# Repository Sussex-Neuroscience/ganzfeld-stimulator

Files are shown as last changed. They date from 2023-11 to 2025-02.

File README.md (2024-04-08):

# ganzfeld-stimulator

## Overview
We built a 'full-field' LED stimulator as a visual stimulus generator for in vivo rodent physiology experiments. The stimulator can generate arbitrary temporal patterns of green and UV light (chromatic channels the mouse visual system is sensitive to) such as high frequency flicker or sinusoidal dimming. Stimulation patterns are generated using PWM signals from a microcontroller.

## Parts 

| Item | Link | Quantity | Cost | Datasheet |
|------|------|----------|------|-----------|
| **LEDS**| | | |
| UV LED   |[C3535U- UNL1-A1G11H-380 TSLC, UV LED, 390nm 480mW 125 °, 2-Pin Surface Mount package](https://uk.rs-online.com/web/p/uv-leds/9033769) | (6 x 6 array) = 36 + any spares | £6.88 each | [From RS](https://uk.rs-online.com/web/p/uv-leds/9033769)|
| Green LED | [ams OSRAM3 V Green LED PLCC 2 SMD, TOPLED LT T673-Q1R2-25](https://uk.rs-online.com/web/p/leds/6648197) | (6 x 6 array) = 36 + any spares | £0.196 each| [From RS](https://uk.rs-online.com/web/p/leds/6648197) |
| LED mounting PCB |  [Custom PCB board for mounting LEDs](repo link) | 6 (Each board is populated with 6 of green and 6 UV) | ?? | 
| Soldering stencil | [Custom stencil](repo link) | 1 | ?? |
|**PSU and Drivers**|||
| LED Driver | [Recom LED Driver, 2 → 35V dc Output, 350mA Output, Constant Current Dimmable](https://uk.rs-online.com/web/p/led-drivers/0416913) | ?? | £12.16 each | [detailed](https://g.recomcdn.com/media/Datasheet/pdf/.fYUQjOlW/.t2a80a771bdbb0ef300f7/Datasheet-93/RCD-24.pdf) |
| PSU | [12V dc Output, 5A Output](https://uk.rs-online.com/web/p/ac-dc-adapters/8808408?gb=s) | ?? | £21.38 each |
|**Box Construction**| | |
| Structure | [MakerBeam starter kit](https://www.technobotsonline.com/makerbeamxl-regular-starter-kit-in-black-anodised-threaded.html) | 1 | £102.95 (possible to buy specific parts separately) | [200mm beam technical drawing](https://drive.google.com/drive/folders/0B8h5C_ek_fmKa2E4a2I1NEtXWTQ?resourcekey=0-tFenALGdWDfK6WEzQJMuUQ), [50mm beam technical drawing](https://drive.google.com/drive/folders/1401xnkoKaVmki9BlENUgdnQiJKWathsU) |
| Structure | [MakerBeam Construction Cubes](https://www.technobotsonline.com/makerbeam-xl-black-corner-cubes-pack-of-12.html) | 1x box of 12 (need 8) |  £18.00 for 12 | [corner cube technical drawing](https://drive.google.com/drive/folders/0B8h5C_ek_fmKcEFvbkl0NWtaZ28?resourcekey=0-kpjmWWiNEXZBVXVSDK05Yg) |
| Reflective Walls + floor | [RS PRO Aluminium Metal Sheet 300mm x 500mm, 2mm Thick](https://uk.rs-online.com/web/p/metal-sheets/0434059) | 1*(200x200mm), 4*(50x200mm) | £49.07 for 5 300x500mm sheets |
|**Diffuser** | | |
| Tracing paper | e.g. [amazon](https://www.amazon.co.uk/GLADFRESIT-Translucent-Architecture-Scrapbooking-Printing/dp/B0C3VX6JPX/ref=asc_df_B0C3VX6JPX/?tag=googshopuk-21&linkCode=df0&hvadid=662823090693&hvpos=&hvnetw=g&hvrand=10142952570193465802&hvpone=&hvptwo=&hvqmt=&hvdev=c&hvdvcmdl=&hvlocint=&hvlocphy=1006565&hvtargid=pla-2196737734548&psc=1&mcid=5f2980b322dd33169770b0c6ecff1379) | 2 sheets + spares | £5.99 |
| Diffusion holder | [Custom 3D printed part](repo link) | ?? | ?? |

## Construction

### Building the stimulator structure
We opted to make a 200x200mm box with a ~50mm depth for achieving a uniform intensity of light. The box can easily be scaled larger and smaller to suit your purposes accordingly.

1) Join 4 x 200mm beams to form a square, using the construction cubes in the corners. You need to make 2 of these for the top and bottom of the box.
2) Cut a ~200x200mm piece of aluminium to slot into the centre of one of the square. You'll need to slightly adjust the size so it fits into the grooves of the beams. This will provide the base for the LED PCBs. (drill a hole of diameter xx for wires)
3) Add 4 x 50mm beams upright to the 4 corners of one of the squares.
4) Screw in the other 200x200mm square to these upright beams to form the top of the box.
5) Cut 4 more pieces of aluminium to form the 4 walls of the box. You want them to be flush with the top of the box to maximise reflectivity of the light inside the box.

### Populating the LEDs on the PCB boards
Use the soldering stencil to populate each of the PCB boards with 6 x green and 6 x UV LEDs. The LEDs are arranged in alternating rows of 3 green/UV.

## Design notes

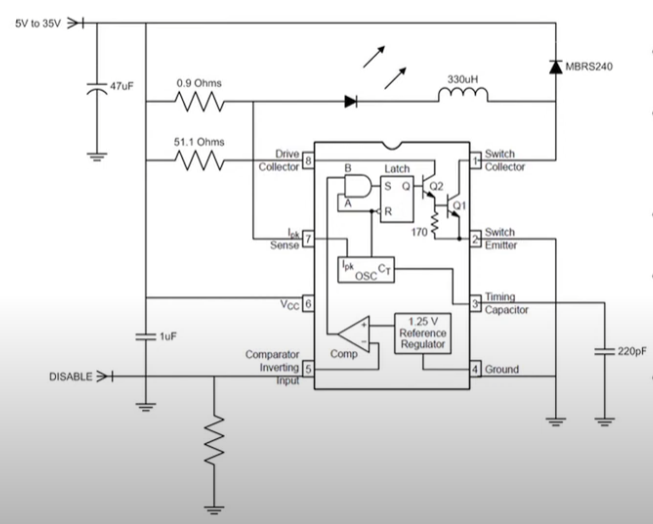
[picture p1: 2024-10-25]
Hardware/PCB/driver circuit.PNG

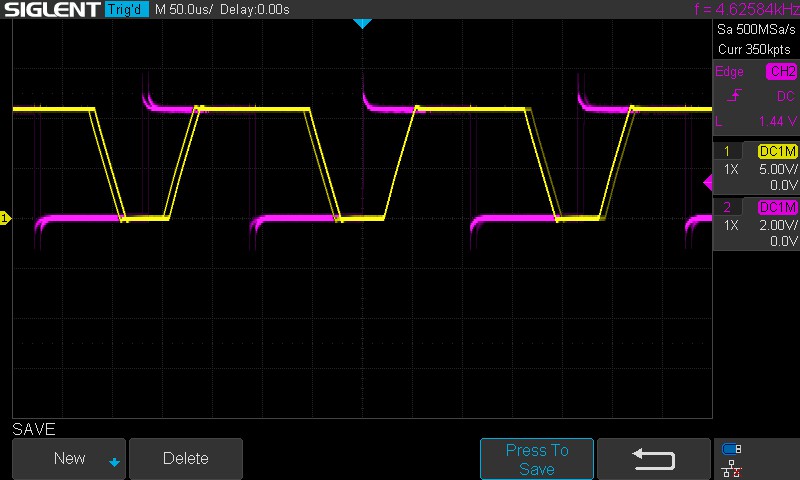
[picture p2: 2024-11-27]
Hardware/PCB/JPG4.62.jpg

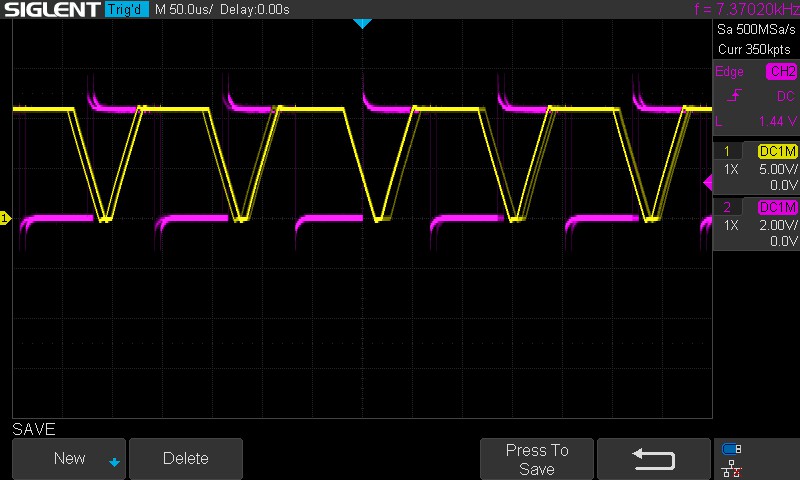
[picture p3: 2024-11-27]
Hardware/PCB/JPG7.37.jpg

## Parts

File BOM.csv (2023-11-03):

qty | component | link
3 | Aluminium sheets | https://uk.rs-online.com/web/p/metal-sheets/0434059
3 | led drivers | https://uk.rs-online.com/web/p/led-drivers/0416913
1 | power supply 12v 5a | https://uk.rs-online.com/web/p/ac-dc-adapters/8808408?gb=s
1 | power connector | https://uk.rs-online.com/web/p/dc-power-connectors/8782606?gb=s
1 | red wire | https://uk.rs-online.com/web/p/hook-up-wire/1225880?gb=s
1 | black wire | https://uk.rs-online.com/web/p/hook-up-wire/1225876?gb=s
2 | pcb board | https://uk.rs-online.com/web/p/copper-clad-boards/2192145?gb=s

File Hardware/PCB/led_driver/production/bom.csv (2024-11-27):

Designator | Footprint | Quantity | Value | LCSC Part #
C1, C5, C6, C8 | CP_Radial_Tantal_D4.5mm_P2.50mm | 4 | 1uF
C2, C3, C4, C7 | CP_Radial_Tantal_D4.5mm_P2.50mm | 4 | C
J1, J3, J4, J8 | JST_XH_B3B-XH-A_1x03_P2.50mm_Vertical | 4 | Conn_01x03_Pin
J2 | JST_XH_B2B-XH-A_1x02_P2.50mm_Vertical | 1 | greenLED
J5, J7, J9 | JST_XH_B2B-XH-A_1x02_P2.50mm_Vertical | 3 | UVLED
J6 | JST_XH_B2B-XH-A_1x02_P2.50mm_Vertical | 1 | power_in
L1, L2, L3, L4 | L_Radial_D6.0mm_P4.00mm | 4 | 22uH
R1, R2, R3, R4 | R_Axial_DIN0411_L9.9mm_D3.6mm_P12.70mm_Horizontal | 4 | R
U1, U2, U3, U4 | Converter_DCDC_RECOM_RCD-24_THT | 4 | RCD-24

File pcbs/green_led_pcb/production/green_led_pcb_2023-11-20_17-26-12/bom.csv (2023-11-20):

Designator | Footprint | Quantity | Value | LCSC Part #
D1, D10, D11, D12, D13, D14, D15, D16, D2, D3, D4, D5, D6, D7, D8, D9 | LED_PLCC-2_3.4x3.0mm_KA | 16 | LED
J1, J2, J3, J4 | PinSocket_1x02_P2.54mm_Horizontal | 4 | Conn_01x02_Socket

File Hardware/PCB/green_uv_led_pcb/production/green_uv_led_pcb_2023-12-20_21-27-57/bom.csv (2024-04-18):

Designator | Footprint | Quantity | Value | LCSC Part #
D1, D10, D11, D2, D3, D9 | LED_PLCC-2_3.4x3.0mm_KA | 6 | LED
D13, D14, D15, D5, D6, D7 | LED_Cree-XP | 6 | LED
H1, H2, H3, H4 | MountingHole_3.2mm_M3 | 4 | MountingHole
J1 | PinSocket_1x02_P2.54mm_Horizontal | 1 | Green bank 1
J2 | PinSocket_1x02_P2.54mm_Horizontal | 1 | UV bank 1
J3 | PinSocket_1x02_P2.54mm_Horizontal | 1 | Green bank 2
J4 | PinSocket_1x02_P2.54mm_Horizontal | 1 | UV bank 2

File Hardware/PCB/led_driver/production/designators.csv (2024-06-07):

C1:1
C2:1
C3:1
C4:1
C5:1
C6:1
C7:1
C8:1
H1:1
H2:1
H3:1
H4:1
J1:1
J2:1
J3:1
J4:1
J5:1
J6:1
J7:1
J8:1
J9:1
L1:1
L2:1
L3:1
L4:1
R1:1
R2:1
R3:1
R4:1
U1:1
U2:1
U3:1
U4:1

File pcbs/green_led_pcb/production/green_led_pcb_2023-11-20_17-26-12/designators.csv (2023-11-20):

D1:1
D10:1
D11:1
D12:1
D13:1
D14:1
D15:1
D16:1
D2:1
D3:1
D4:1
D5:1
D6:1
D7:1
D8:1
D9:1
J1:1
J2:1
J3:1
J4:1

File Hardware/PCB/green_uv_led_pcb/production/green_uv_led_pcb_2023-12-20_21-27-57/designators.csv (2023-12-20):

D1:1
D10:1
D11:1
D13:1
D14:1
D15:1
D2:1
D3:1
D5:1
D6:1
D7:1
D9:1
H1:1
H2:1
H3:1
H4:1
J1:1
J2:1
J3:1
J4:1

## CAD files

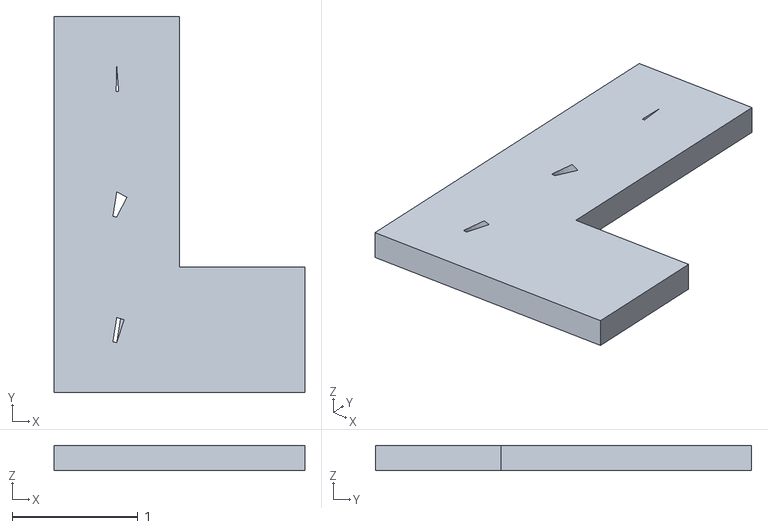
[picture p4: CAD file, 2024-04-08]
3d_printing/3rdPartyParts/LBracketb.stl
2.00 x 3.00 x 0.2

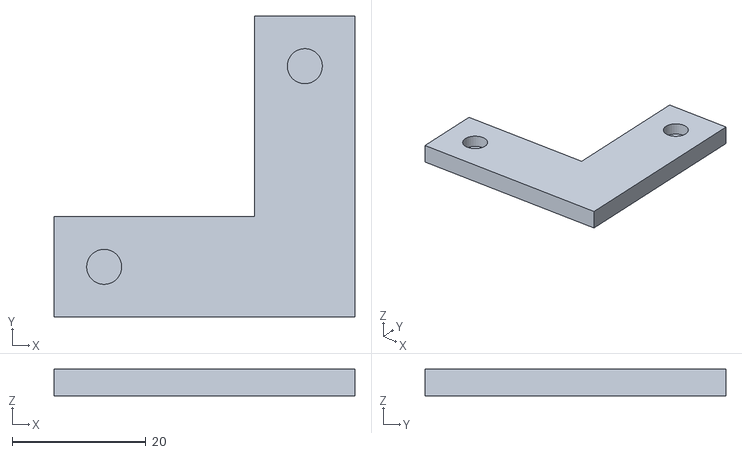
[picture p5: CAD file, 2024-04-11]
3d_printing/CustomRBracket_magnet.stl
45.0 x 45.0 x 4.00

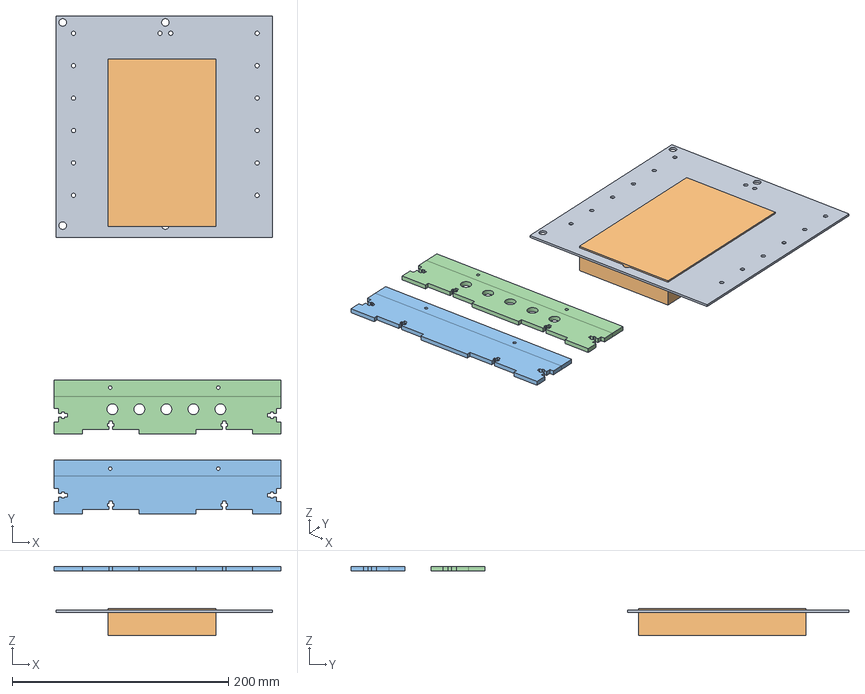
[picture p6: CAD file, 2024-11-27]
Hardware/CAD/Designs/StimulatorHousing.FCStd
210.0 x 461.0 x 64.0 mm
Bottom+holes
Electronics

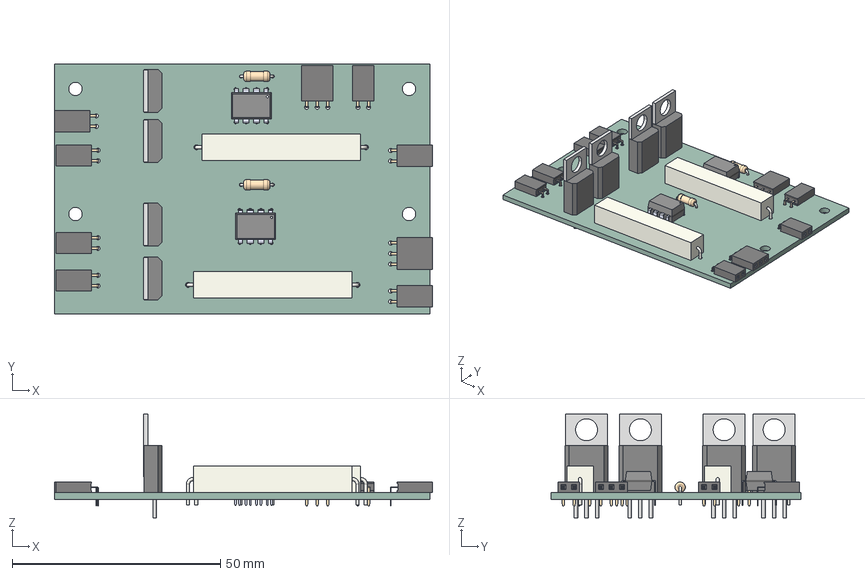
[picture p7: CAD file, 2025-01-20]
Hardware/PCB/custom_driver/custom_driver.step
90.7 x 60.0 x 24.9 mm
PinSocket_1x02_P254mm_Horizontal x 7
R_Axial_DIN0207_L63mm_D25mm_P762mm_Horizontal x 2
P8 x 2
PinSocket_1x03_P254mm_Horizontal x 2
R_Axial_Power_L380mm_W64mm_P4064mm x 2
_autosave-custom_driver_PCB

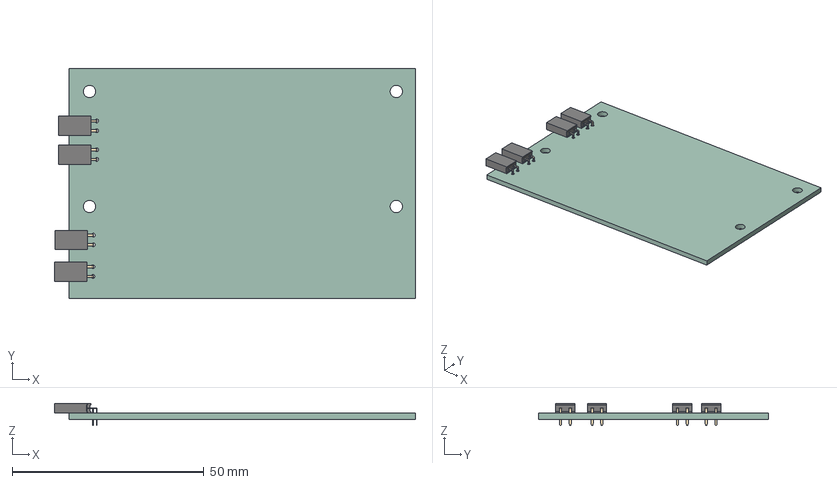
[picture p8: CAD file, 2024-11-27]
Hardware/PCB/green_uv_led_pcb/green_uv_led_pcb.step
94.1 x 60.0 x 5.84 mm
PinSocket_1x02_P254mm_Horizontal x 4
green_uv_led_pcb_PCB

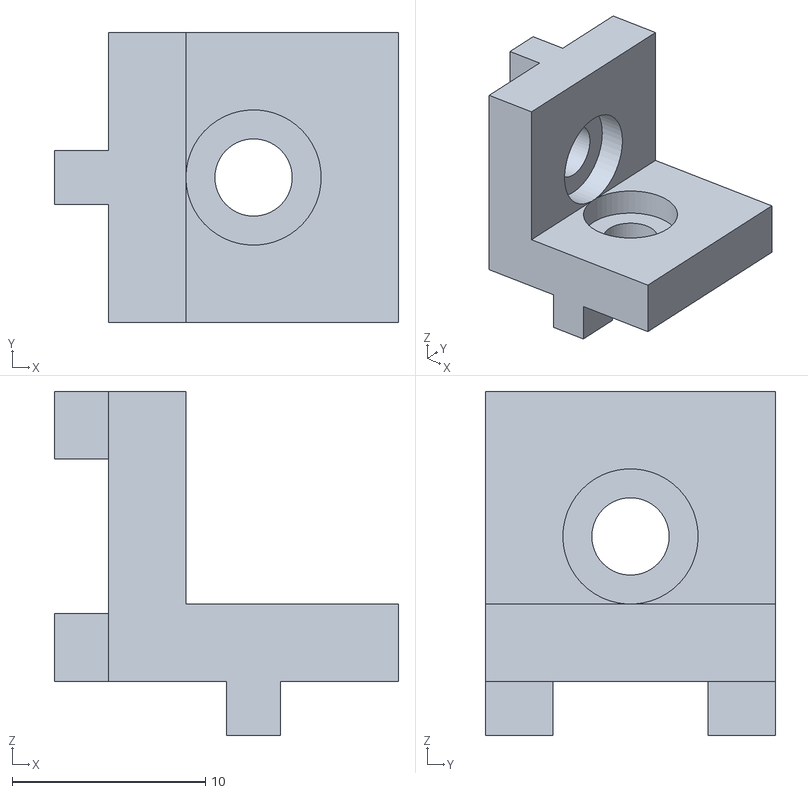
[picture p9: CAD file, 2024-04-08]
3d_printing/3rdPartyParts/corner_cross_90.stl
17.8 x 15.0 x 17.8

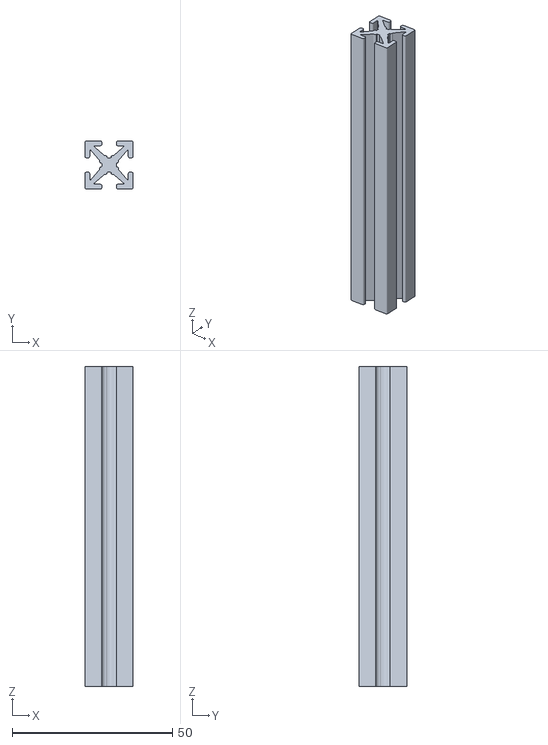
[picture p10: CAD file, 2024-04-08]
3d_printing/3rdPartyParts/MakerBeamXL_100mm.stl
15.0 x 15.0 x 100.0

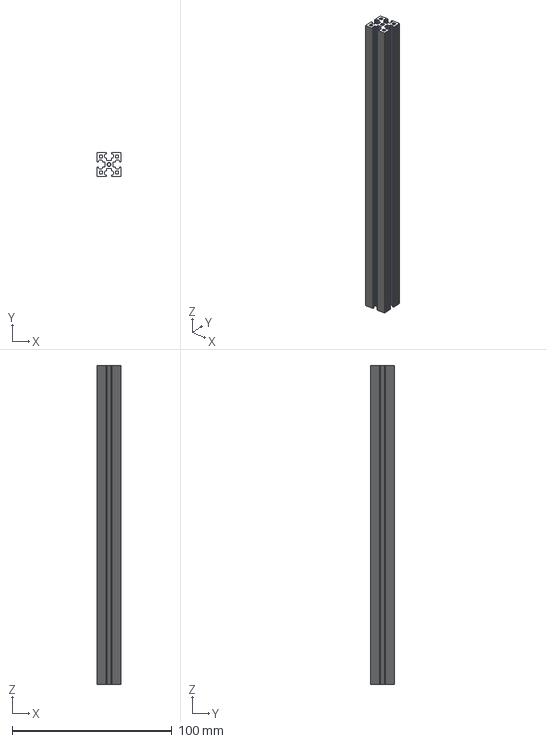
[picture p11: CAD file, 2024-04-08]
Hardware/CAD/Mnf. specs/200mmBeams/103161.stp
15.0 x 15.0 x 200.0 mm

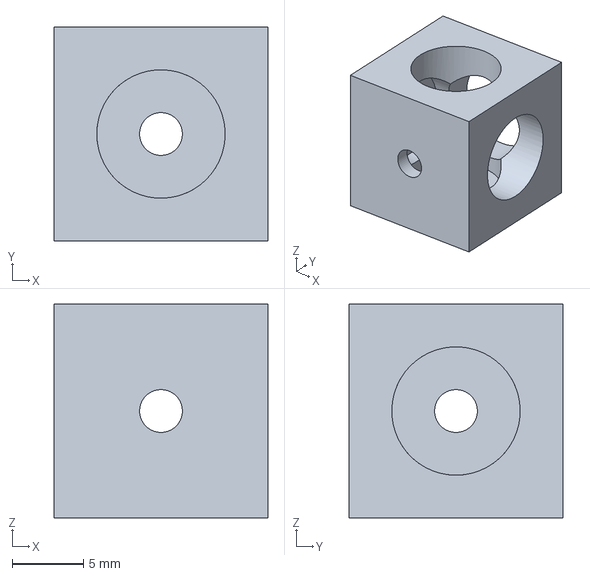
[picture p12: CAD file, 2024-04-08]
Hardware/CAD/Mnf. specs/ConstructionCubesXL/103105.stp
15.0 x 15.0 x 15.0 mm

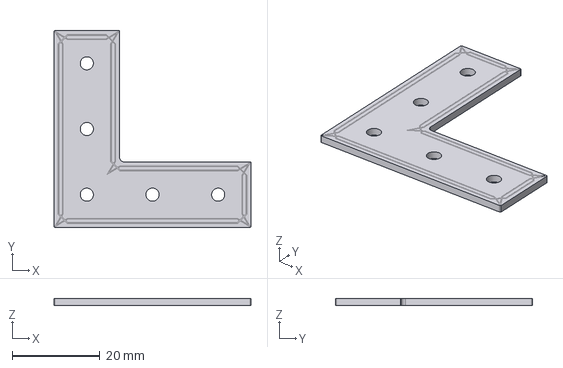
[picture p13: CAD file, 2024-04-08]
Hardware/CAD/Mnf. specs/RightAngleBracket_XL/101732.stp
45.0 x 45.0 x 1.50 mm

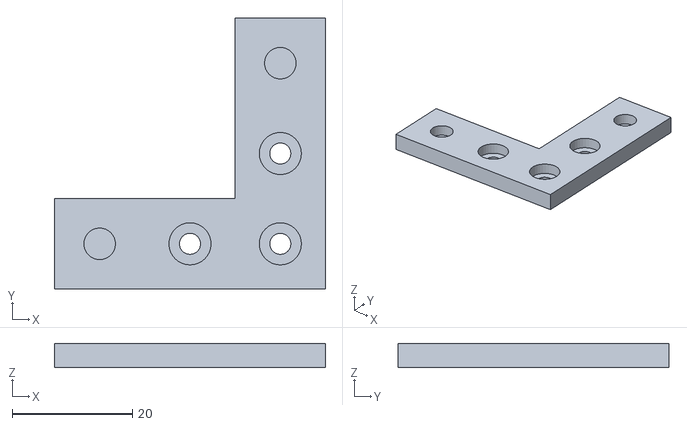
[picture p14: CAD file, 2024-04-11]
3d_printing/CustomRBracket_screwAndMagnetHoles.stl
45.0 x 45.0 x 4.00

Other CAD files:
3d_printing/3rdPartyParts/corner_90.stl
Hardware/CAD/Archive/3rdPartyParts/corner_90.stl
Hardware/CAD/Mnf. specs/200mmBeams/103161.dxf
Hardware/CAD/Mnf. specs/ConstructionCubesXL/103105.dxf
Hardware/CAD/Mnf. specs/RightAngleBracket_XL/101732.dxf

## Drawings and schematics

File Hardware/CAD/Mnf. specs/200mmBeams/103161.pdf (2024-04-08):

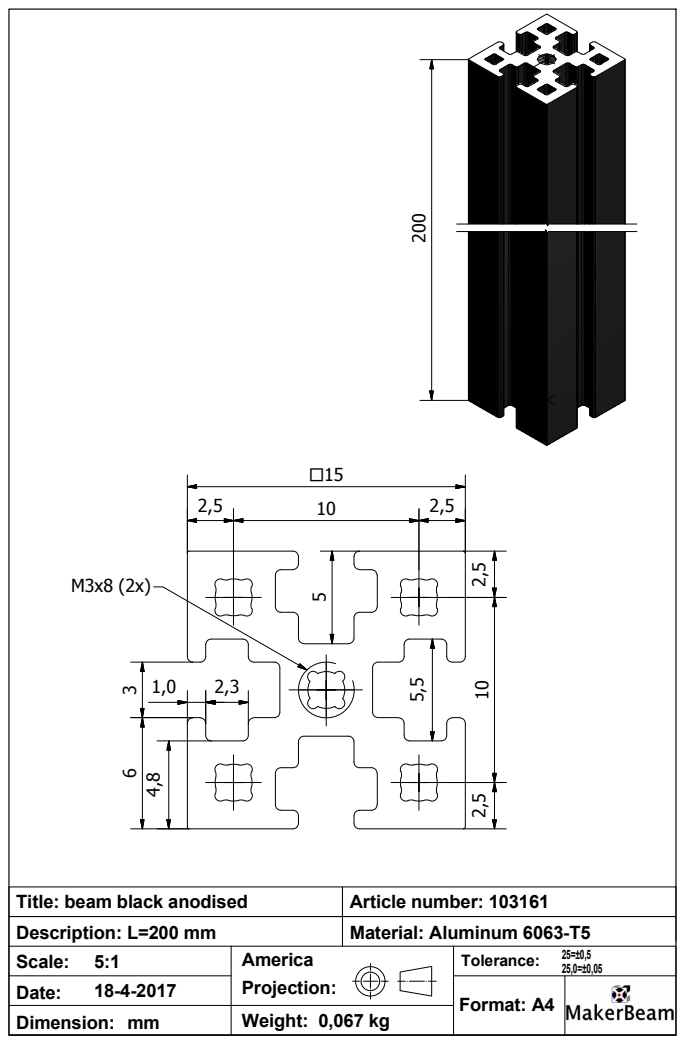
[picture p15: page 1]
America; Weight: 0,067 kg; 25=±0,5 Scale:; Date:; Dimension: mm; Format: A4; Tolerance:; Article number: 103161; Description: L=200 mm; Material: Aluminum 6063-T5; Projection:

Title: beam black anodised

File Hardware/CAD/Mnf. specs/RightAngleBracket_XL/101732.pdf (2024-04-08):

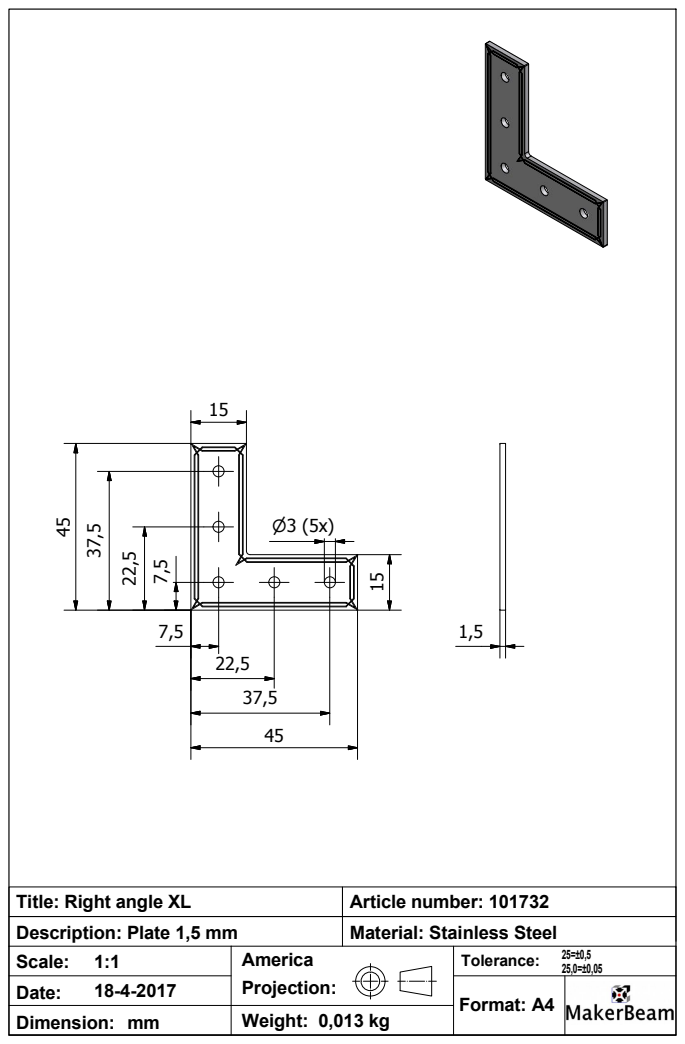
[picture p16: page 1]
America; Weight: 0,013 kg; 25=±0,5 Scale:; Date:; Dimension: mm; Format: A4; Tolerance:; Article number: 101732; Description: Plate 1,5 mm; Material: Stainless Steel; Projection:

Title: Right angle XL

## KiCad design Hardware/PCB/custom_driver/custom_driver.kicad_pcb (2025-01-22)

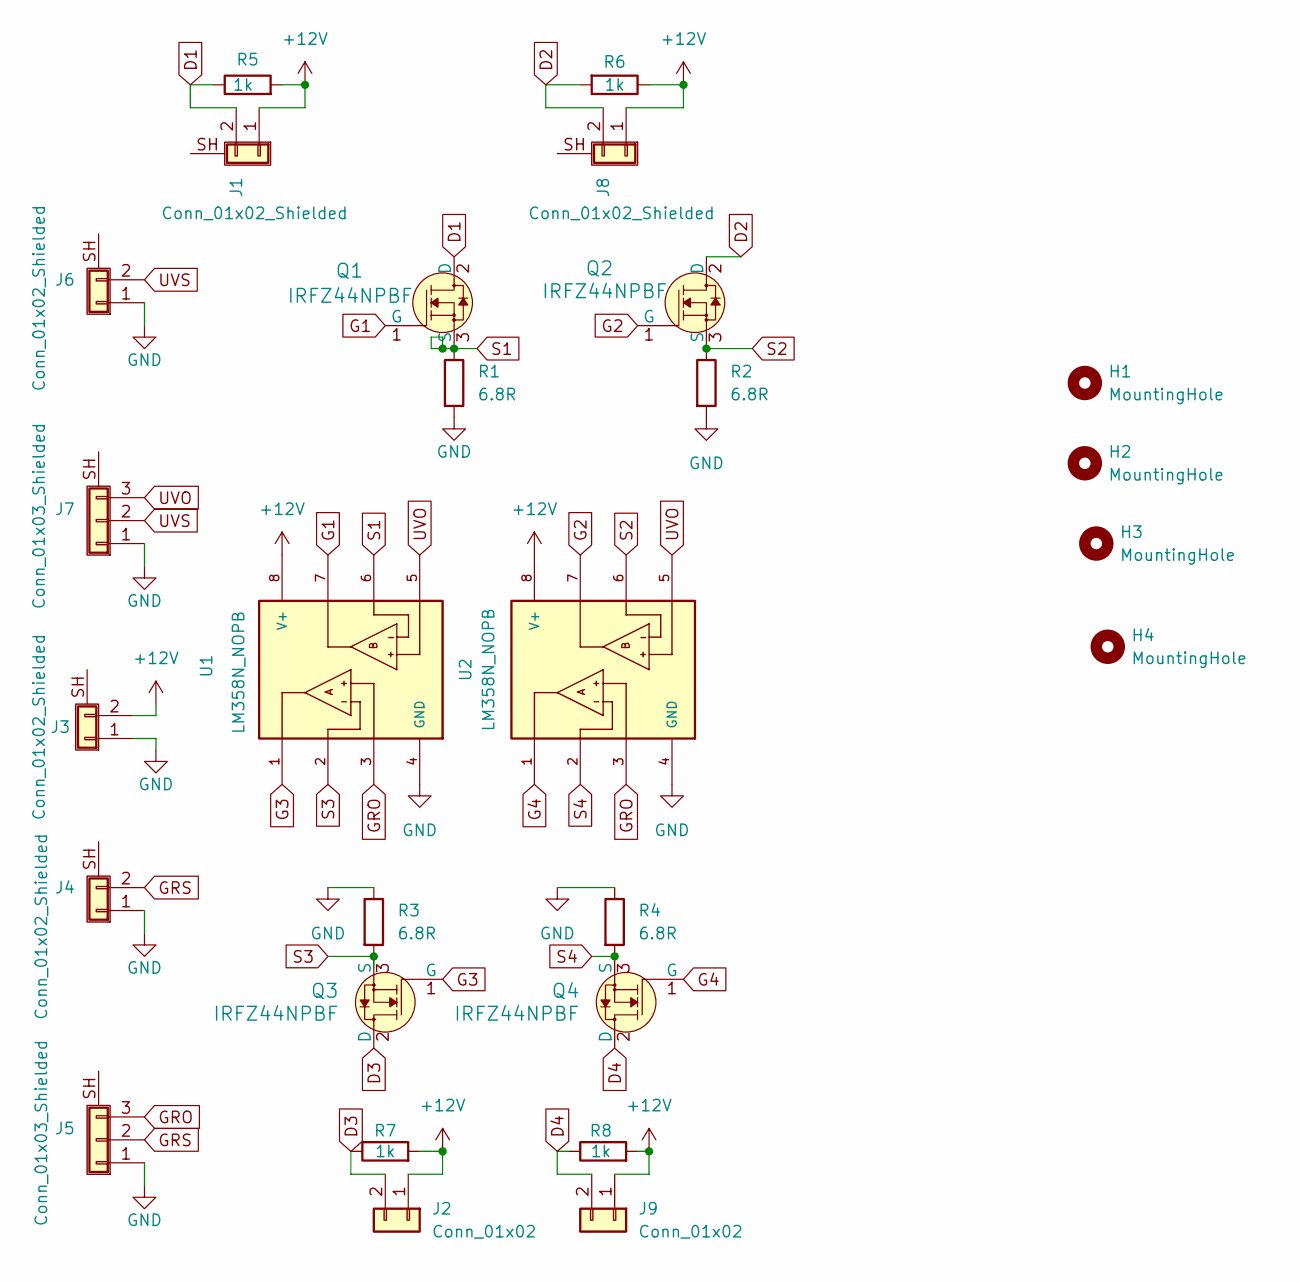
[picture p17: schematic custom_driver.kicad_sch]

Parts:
H1, H2, H3, H4: MountingHole; MountingHole_3.2mm_M3
J1, J3, J4, J6, J8: Conn_01x02_Shielded; PinSocket_1x02_P2.54mm_Horizontal
J2, J9: Conn_01x02; PinSocket_1x02_P2.54mm_Horizontal
J5, J7: Conn_01x03_Shielded; PinSocket_1x03_P2.54mm_Horizontal
Q1, Q2, Q3, Q4: IRFZ44NPBF; TO-220-3; MPN IRF510PBF; Digi-Key_PN IRF510PBF-ND
R1, R2: 6.8R; R_Axial_Power_L38.0mm_W6.4mm_P40.64mm
R3, R4: 6.8R; R_Axial_DIN0207_L6.3mm_D2.5mm_P7.62mm_Horizontal
R5, R6, R7, R8: 1k; R_Axial_DIN0207_L6.3mm_D2.5mm_P7.62mm_Horizontal
U1, U2: LM358N_NOPB; LM358N_NOP

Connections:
+12V: J1.1, J2.1, J3.2, J8.1, J9.1, R5.2, R6.1, R7.2, R8.2, U1.8 (V+), U2.8 (V+)
D1: J1.2, Q1.2 (D), R5.1
D2: J8.2, Q2.2 (D), R6.2
D3: J2.2, Q3.2 (D), R7.1
D4: J9.2, Q4.2 (D), R8.1
G1: Q1.1 (G), U1.7
G2: Q2.1 (G), U2.7
G3: Q3.1 (G), U1.1
G4: Q4.1 (G), U2.1
GND: J3.1, J4.1, J5.1, J6.1, J7.1, R1.2, R2.2, R3.1, R4.1, U1.4 (GND), U2.4 (GND)
GRO: J5.3, U1.3, U2.3
GRS: J4.2, J5.2
S1: Q1.3 (S), R1.1, U1.6
S2: Q2.3 (S), R2.1, U2.6
S3: Q3.3 (S), R3.2, U1.2
S4: Q4.3 (S), R4.2, U2.2
UVO: J7.3, U1.5, U2.5
UVS: J6.2, J7.2

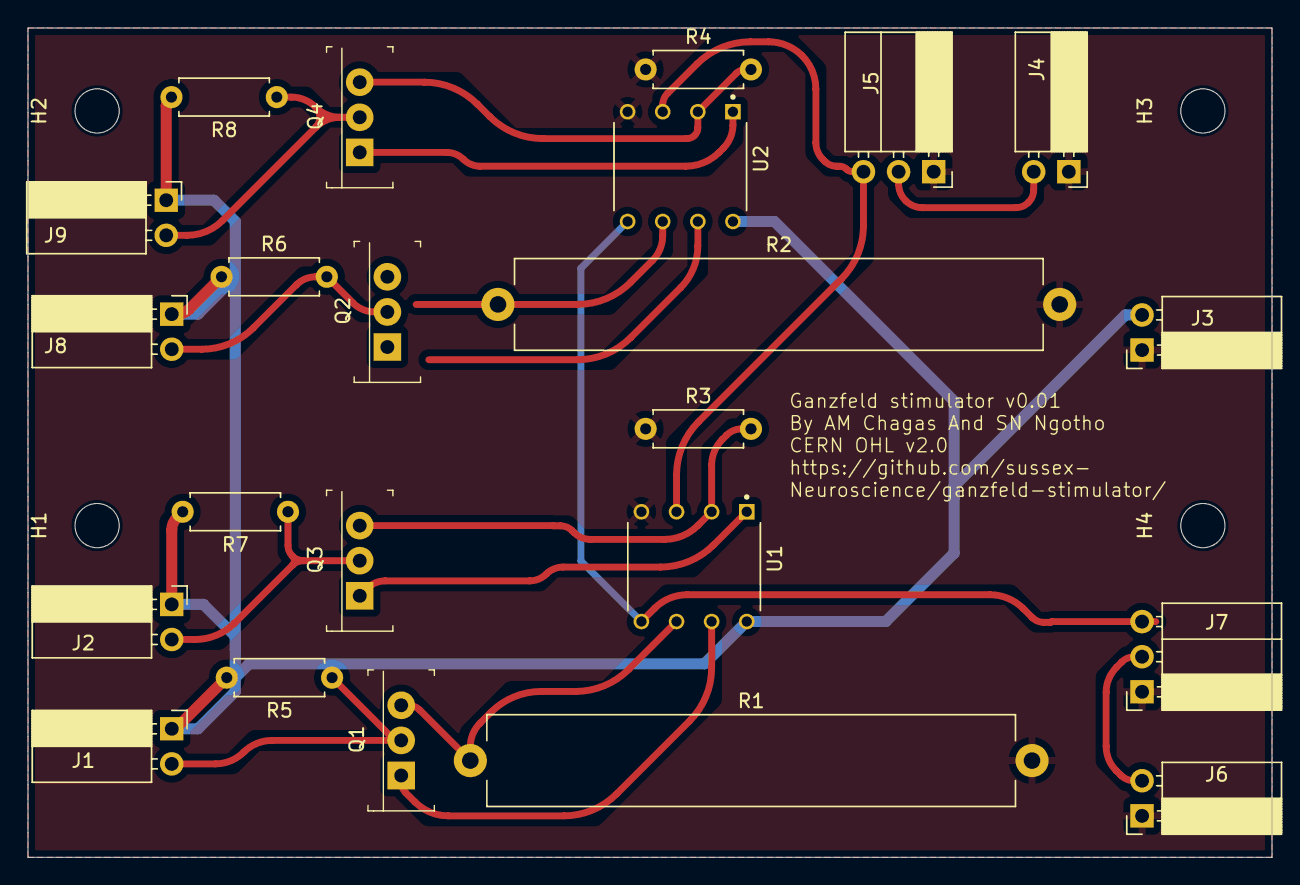
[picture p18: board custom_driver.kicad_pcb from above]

Board: 2 copper layers, 90.0 x 60.0 mm, 27 parts (0 on the bottom side), 18 nets.

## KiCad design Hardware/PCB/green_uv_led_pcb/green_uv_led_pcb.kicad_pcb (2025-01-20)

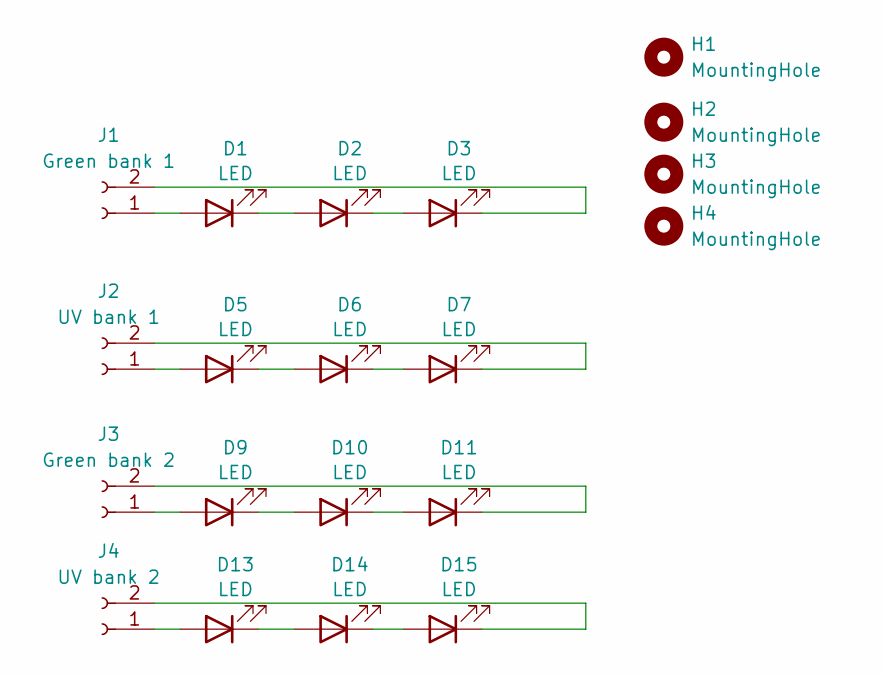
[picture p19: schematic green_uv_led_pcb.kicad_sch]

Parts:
D1, D2, D3, D9, D10, D11: LED; LED_PLCC-2_3.4x3.0mm_KA
D5, D6, D7, D13, D14, D15: LED; LED_Cree-XP
H1, H2, H3, H4: MountingHole; MountingHole_3.2mm_M3
J1: Green bank 1; PinSocket_1x02_P2.54mm_Horizontal
J2: UV bank 1; PinSocket_1x02_P2.54mm_Horizontal
J3: Green bank 2; PinSocket_1x02_P2.54mm_Horizontal
J4: UV bank 2; PinSocket_1x02_P2.54mm_Horizontal

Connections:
unnamed: D1.2 (A), J1.1
unnamed: D1.1 (K), D2.2 (A)
unnamed: D2.1 (K), D3.2 (A)
unnamed: D3.1 (K), J1.2
unnamed: D5.2 (A), J2.1
unnamed: D5.1 (K), D6.2 (A)
unnamed: D6.1 (K), D7.2 (A)
unnamed: D7.1 (K), J2.2
unnamed: D9.2 (A), J3.1
unnamed: D9.1 (K), D10.2 (A)
unnamed: D10.1 (K), D11.2 (A)
unnamed: D11.1 (K), J3.2
unnamed: D13.2 (A), J4.1
unnamed: D13.1 (K), D14.2 (A)
unnamed: D14.1 (K), D15.2 (A)
unnamed: D15.1 (K), J4.2

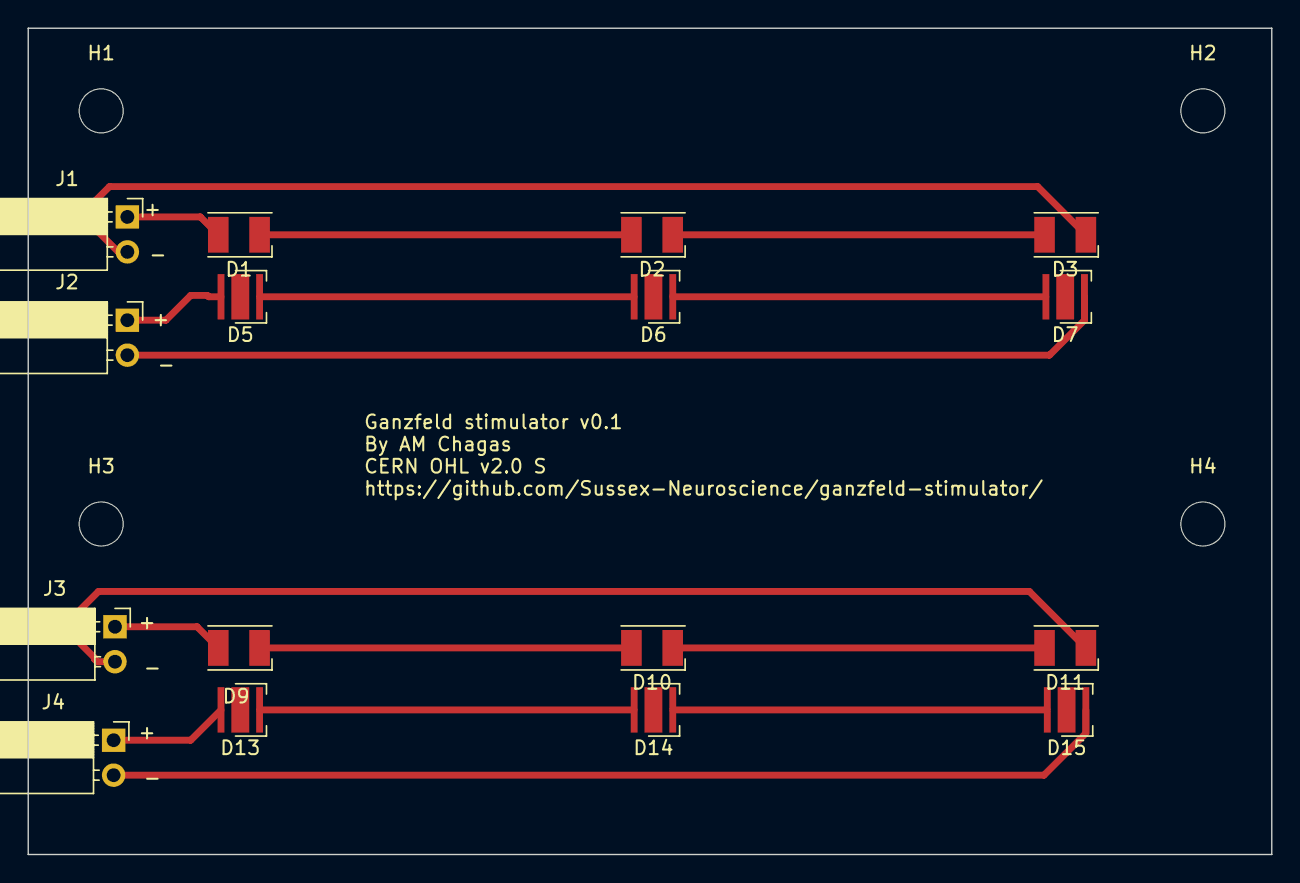
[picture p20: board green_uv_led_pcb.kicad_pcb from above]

Board: 2 copper layers, 90.3 x 60.0 mm, 20 parts (0 on the bottom side), 16 nets.

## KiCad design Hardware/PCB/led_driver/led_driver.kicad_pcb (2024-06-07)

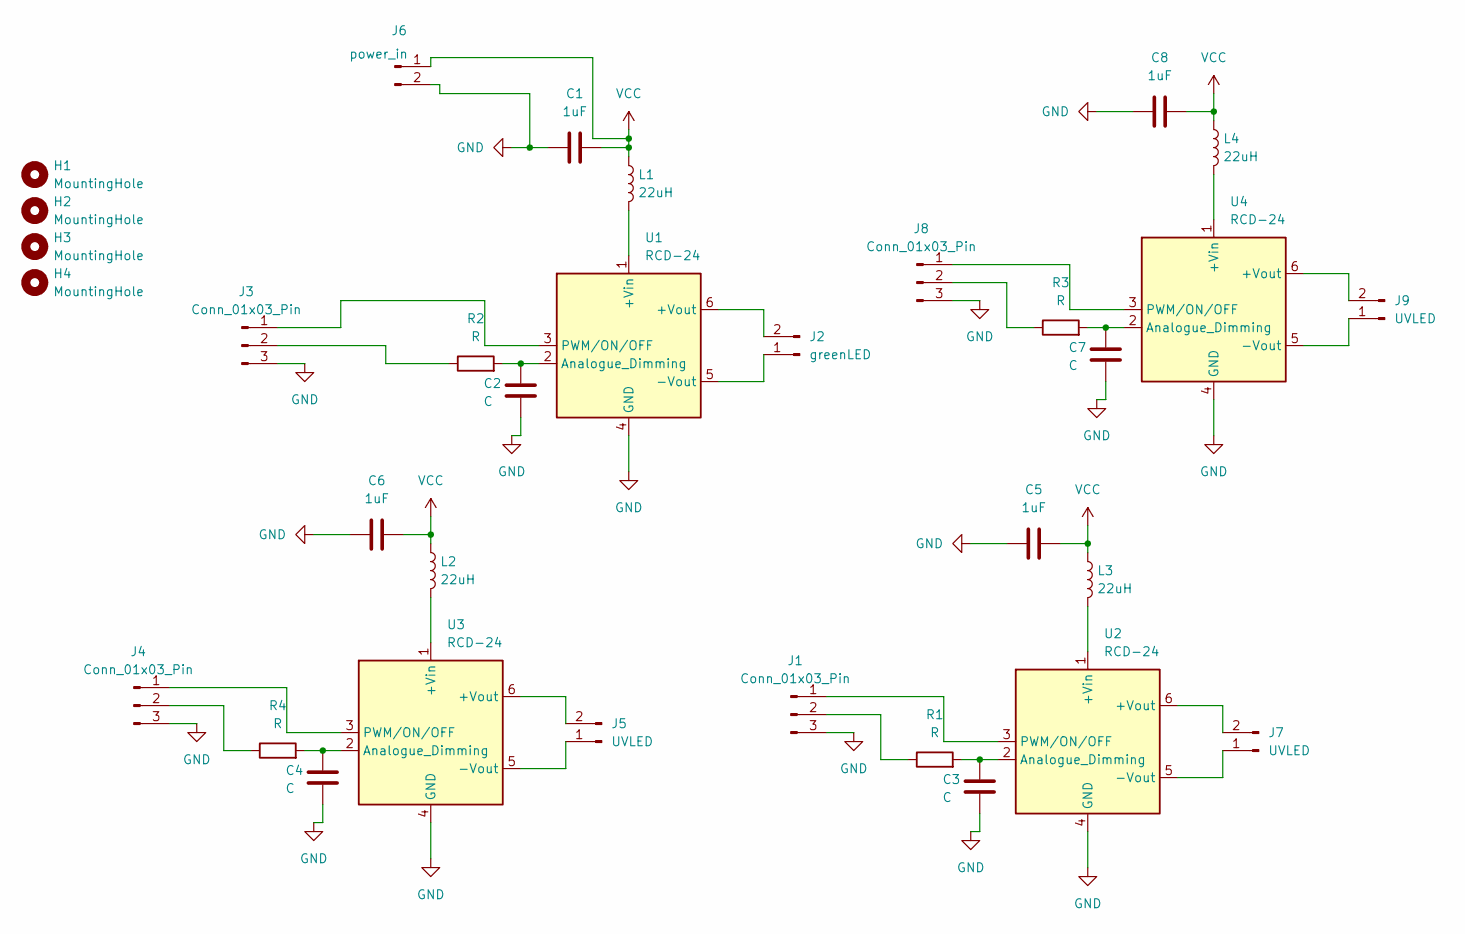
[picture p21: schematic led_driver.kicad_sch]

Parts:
C1, C5, C6, C8: 1uF; CP_Radial_Tantal_D4.5mm_P2.50mm
C2, C3, C4, C7: C; CP_Radial_Tantal_D4.5mm_P2.50mm
H1, H2, H3, H4: MountingHole; MountingHole_3.2mm_M3
J1, J3, J4, J8: Conn_01x03_Pin; JST_XH_B3B-XH-A_1x03_P2.50mm_Vertical
J2: greenLED; JST_XH_B2B-XH-A_1x02_P2.50mm_Vertical
J5, J7, J9: UVLED; JST_XH_B2B-XH-A_1x02_P2.50mm_Vertical
J6: power_in; JST_XH_B2B-XH-A_1x02_P2.50mm_Vertical
L1, L2, L3, L4: 22uH; L_Radial_D6.0mm_P4.00mm
R1, R2, R3, R4: R; R_Axial_DIN0411_L9.9mm_D3.6mm_P12.70mm_Horizontal
U1, U2, U3, U4: RCD-24; Converter_DCDC_RECOM_RCD-24_THT

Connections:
GND: C1.1, C2.2, C3.2, C4.2, C5.1, C6.1, C7.2, C8.1, J1.3, J3.3, J4.3, J6.2, J8.3, U1.4 (GND), U2.4 (GND), U3.4 (GND), U4.4 (GND)
unnamed: J1.1, U2.3 (PWM/ON/OFF)
unnamed: J1.2, R1.1
unnamed: J2.1, U1.5 (-Vout)
unnamed: J2.2, U1.6 (+Vout)
unnamed: J3.1, U1.3 (PWM/ON/OFF)
unnamed: J3.2, R2.1
unnamed: J4.1, U3.3 (PWM/ON/OFF)
unnamed: J4.2, R4.1
unnamed: J5.1, U3.5 (-Vout)
unnamed: J5.2, U3.6 (+Vout)
unnamed: J7.1, U2.5 (-Vout)
unnamed: J7.2, U2.6 (+Vout)
unnamed: J8.1, U4.3 (PWM/ON/OFF)
unnamed: J8.2, R3.1
unnamed: J9.1, U4.5 (-Vout)
unnamed: J9.2, U4.6 (+Vout)
unnamed: L1.2, U1.1 (+Vin)
unnamed: C2.1, R2.2, U1.2 (Analogue_Dimming)
unnamed: L3.2, U2.1 (+Vin)
unnamed: C3.1, R1.2, U2.2 (Analogue_Dimming)
unnamed: L2.2, U3.1 (+Vin)
unnamed: C4.1, R4.2, U3.2 (Analogue_Dimming)
unnamed: L4.2, U4.1 (+Vin)
unnamed: C7.1, R3.2, U4.2 (Analogue_Dimming)
VCC: C1.2, C5.2, C6.2, C8.2, J6.1, L1.1, L2.1, L3.1, L4.1

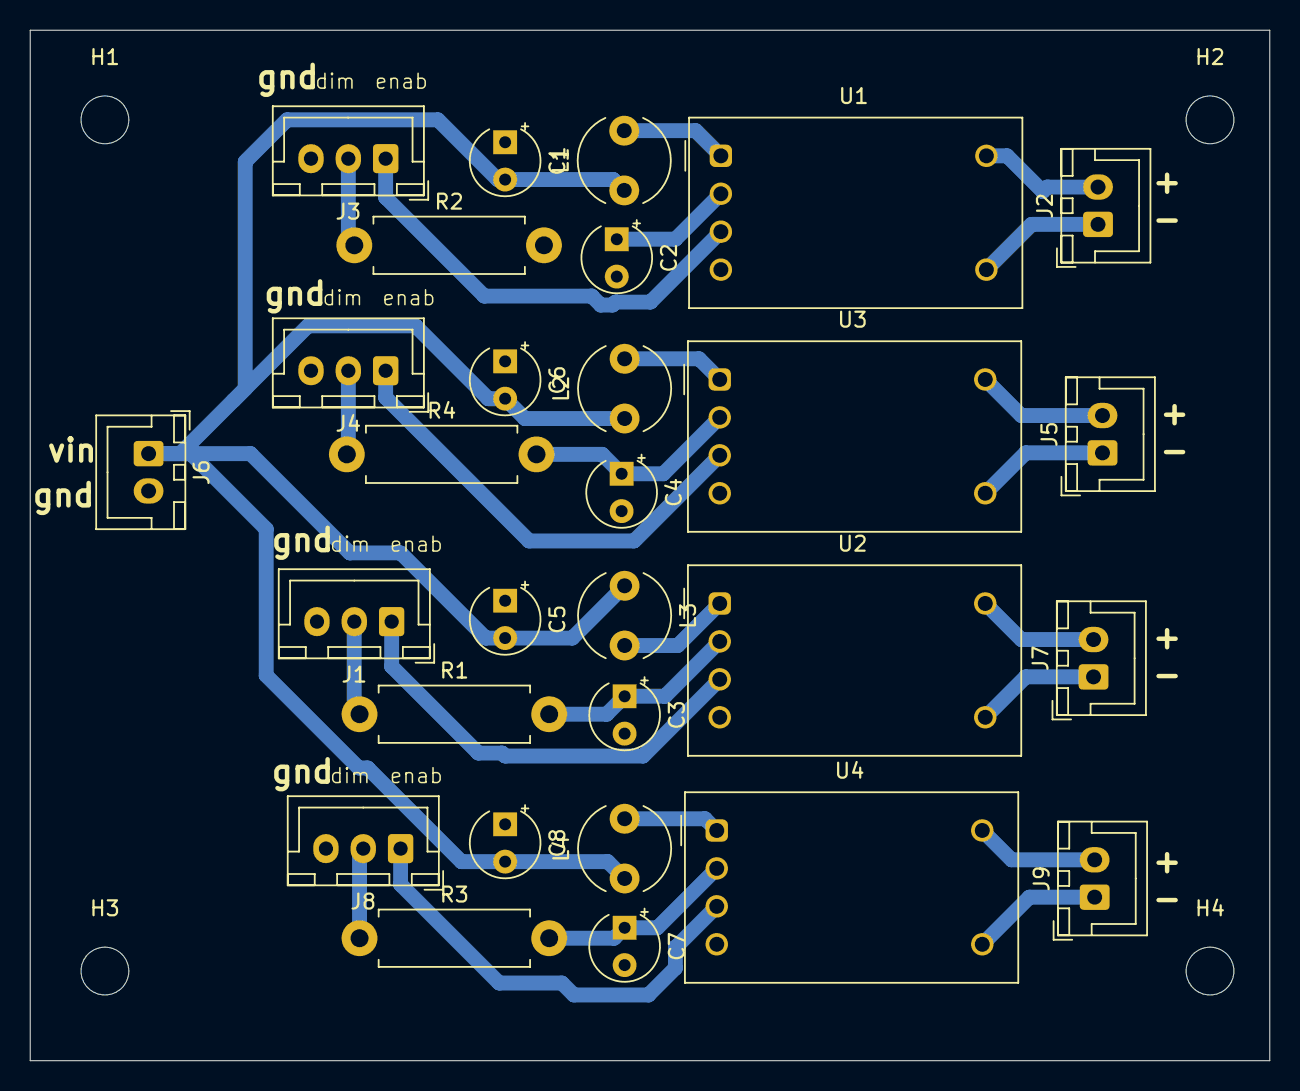
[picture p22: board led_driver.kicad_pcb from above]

Board: 2 copper layers, 83.0 x 69.0 mm, 33 parts (0 on the bottom side), 26 nets.

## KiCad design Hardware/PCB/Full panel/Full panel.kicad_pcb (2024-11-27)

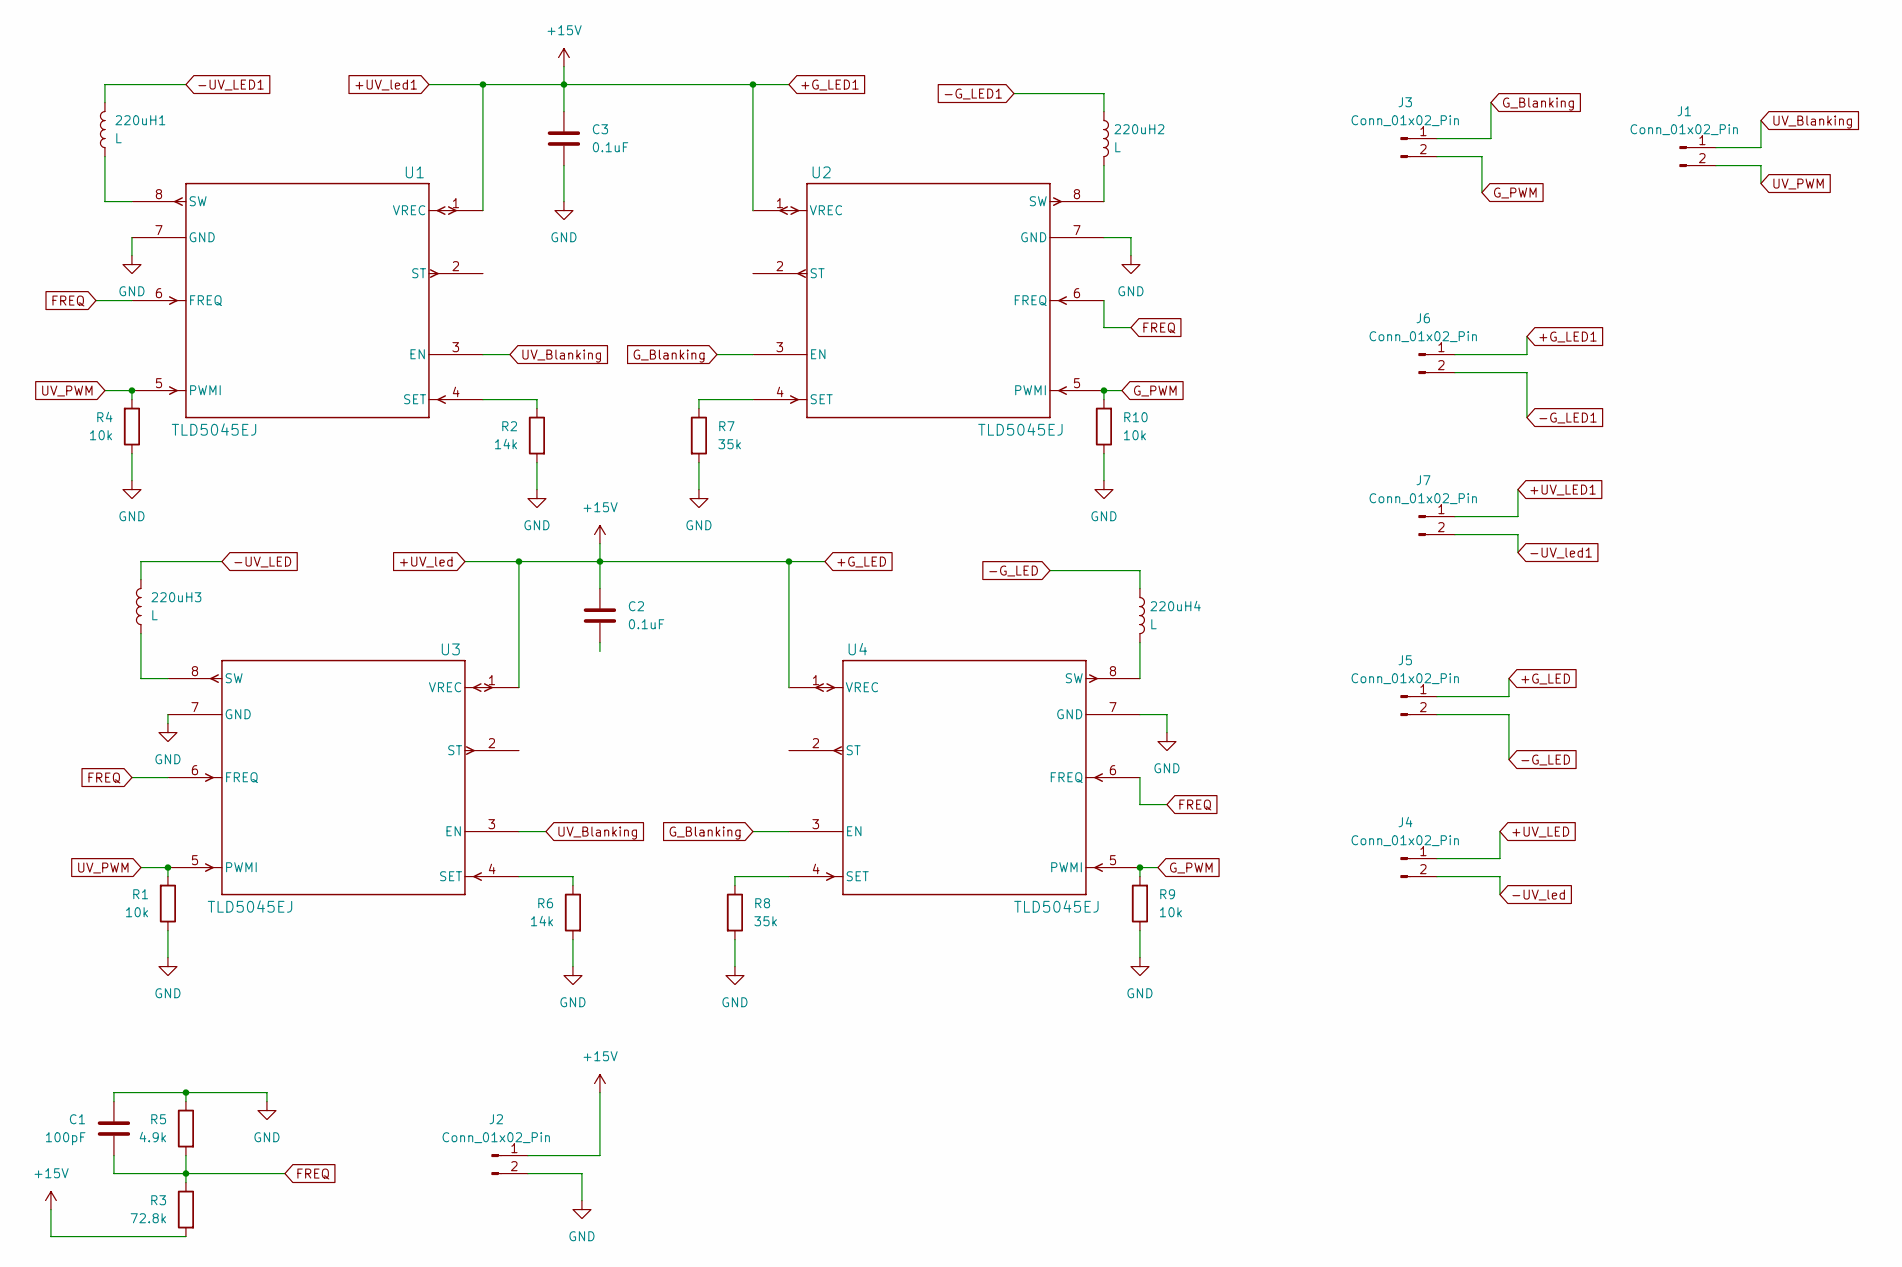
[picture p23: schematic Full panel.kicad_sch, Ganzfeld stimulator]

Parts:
220uH1, 220uH2, 220uH3, 220uH4: L; C_0805_2012Metric_Pad1.18x1.45mm_HandSolder
C1: 100pF; C_0805_2012Metric_Pad1.18x1.45mm_HandSolder
C2, C3: 0.1uF; C_0805_2012Metric_Pad1.18x1.45mm_HandSolder
J1, J2, J3, J4, J5, J6, J7: Conn_01x02_Pin; PinSocket_1x02_P2.54mm_Vertical
R1, R4, R9, R10: 10k; C_0805_2012Metric_Pad1.18x1.45mm_HandSolder
R2, R6: 14k; C_0805_2012Metric_Pad1.18x1.45mm_HandSolder
R3: 72.8k; C_0805_2012Metric_Pad1.18x1.45mm_HandSolder
R5: 4.9k; C_0805_2012Metric_Pad1.18x1.45mm_HandSolder
R7, R8: 35k; C_0805_2012Metric_Pad1.18x1.45mm_HandSolder
U1, U2, U3, U4: TLD5045EJ; PG-DSO-8-1_INF

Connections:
+G_LED: C2.1, C3.1, J2.1, J5.1, J6.1, R3.2, U1.1 (VREC), U2.1 (VREC), U3.1 (VREC), U4.1 (VREC)
+UV_LED: J4.1
+UV_LED1: J7.1
-G_LED: 220uH4.1, J5.2
-G_LED1: 220uH2.1, J6.2
-UV_LED: 220uH3.1
-UV_LED1: 220uH1.1
-UV_led: J4.2
-UV_led1: J7.2
FREQ: C1.2, R3.1, R5.2, U1.6 (FREQ), U2.6 (FREQ), U3.6 (FREQ), U4.6 (FREQ)
GND: C1.1, C3.2, J2.2, R1.1, R2.2, R4.1, R5.1, R6.2, R7.2, R8.2, R9.1, R10.1, U1.7 (GND), U2.7 (GND), U3.7 (GND), U4.7 (GND)
G_Blanking: J3.1, U2.3 (EN), U4.3 (EN)
G_PWM: J3.2, R9.2, R10.2, U2.5 (PWMI), U4.5 (PWMI)
unnamed: R2.1, U1.4 (SET)
unnamed: 220uH1.2, U1.8 (SW)
unnamed: R7.1, U2.4 (SET)
unnamed: 220uH2.2, U2.8 (SW)
unnamed: R6.1, U3.4 (SET)
unnamed: 220uH3.2, U3.8 (SW)
unnamed: R8.1, U4.4 (SET)
unnamed: 220uH4.2, U4.8 (SW)
UV_Blanking: J1.1, U1.3 (EN), U3.3 (EN)
UV_PWM: J1.2, R1.2, R4.2, U1.5 (PWMI), U3.5 (PWMI)

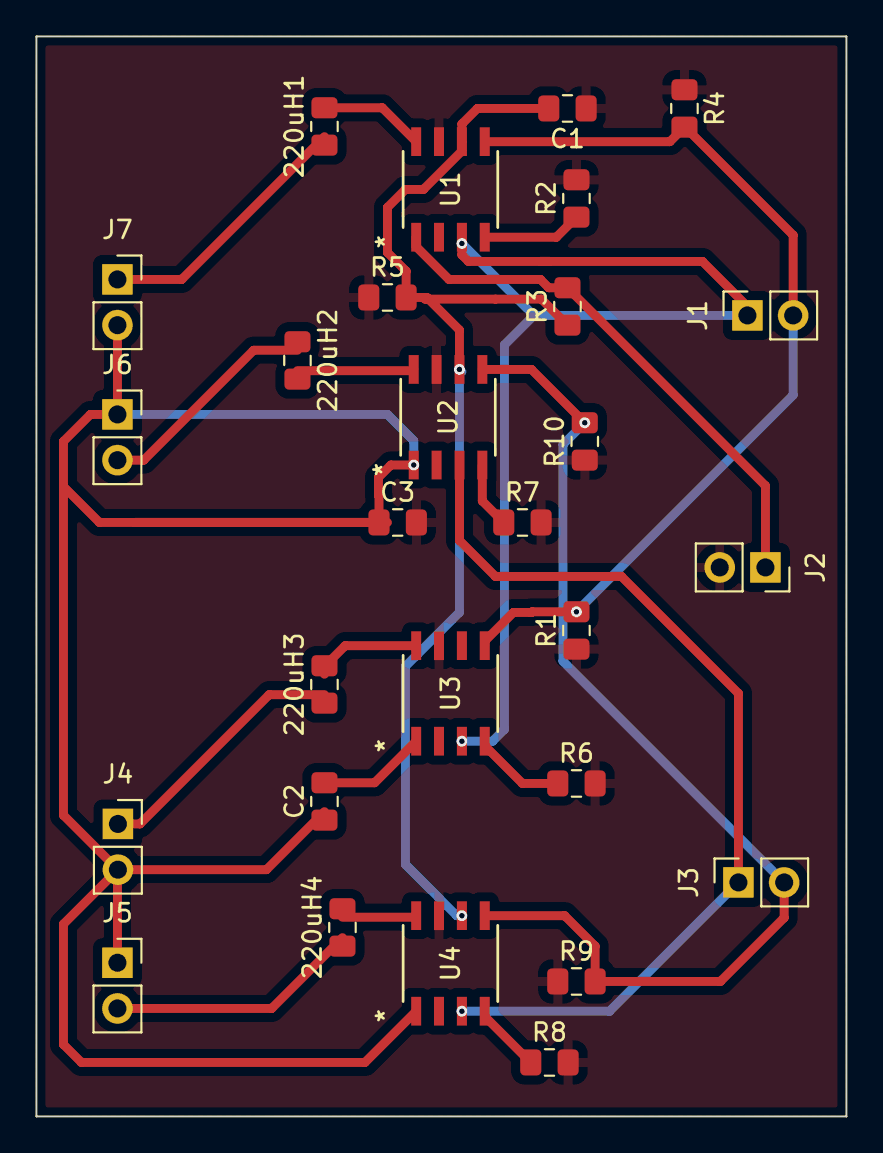
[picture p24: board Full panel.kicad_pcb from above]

Board: 2 copper layers, 45.0 x 60.0 mm, 28 parts (0 on the bottom side), 17 nets.

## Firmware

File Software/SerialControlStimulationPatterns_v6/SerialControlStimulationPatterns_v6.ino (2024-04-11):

// To do:
// 1) Set vars to 0 once stimulus has run to prevent accidental leak to subsequent stimuli
// 2) check valid vars (mainly nonzero) before running stimuli. Otherwise return a serial error message

// constants won't change:
const int ledPin =  3;// the number of the LED pin

// serial
const byte numChars = 30;
char receivedChars[numChars];   // an array to store the received data
bool newData = false;

// stimulus selection char
String FirstChar;

// generic stimulus duration var
float stimulusDuration;

// vars for flicker and sinusoidal dimming
float frequency;

// vars for temporal contrast switching
float contrastSwitchTime;
float ledUpdateTime;

// vars for flicker-sine convolution
float carrierFrequency;



void setup() {
  // set the digital pin as output:
  pinMode(ledPin, OUTPUT);
  digitalWrite(ledPin, LOW);
  Serial.begin(9600);
  Serial.setTimeout(5);

  delay(500);

}

void loop() {
  GetSerialInput();
  if (newData)
  {
    newData = false;
    ActionSerial();
  }
}

void GetSerialInput() { // part of code taken from http://forum.arduino.cc/index.php?topic=396450.0
  static byte ndx = 0;
  char endMarker = '\r';
  char rc;
  if (Serial.available() > 0) {
    rc = Serial.read();
    if (rc != endMarker) {
      receivedChars[ndx] = rc;
      ndx++;
      if (ndx >= numChars) {
        ndx = numChars - 1;
      }
    }
    else { // serial message finished
      receivedChars[ndx] = '\0'; // terminate the string
      ndx = 0;
      newData = true;
      }
  }      
}

void ActionSerial() { // Actions serial data by choosing appropriate stimulation
  Serial.print("rc: ");
  Serial.println(receivedChars);
  char delimiters[] = ",";
  char *token;
  uint8_t  idx = 0;
  #define MAX_VALS    5 // max required? freq, duration, contrast, carrier freq?
  char *serialVals[MAX_VALS];
  token = strtok( receivedChars, "," );
  
  
  while( token != NULL ) 
  {
    //Serial.println( token );
    if( idx < MAX_VALS )
    serialVals[idx++] = token;
    token = strtok( NULL, "," );
  }

        FirstChar = serialVals[0];

        if (FirstChar == "f") // flicker
        {
          stimulusDuration = atof(serialVals[1]);
          frequency = atof(serialVals[2]);
          Serial.println("Stim: Flicker");
          Serial.print("Stim duration: ");
          Serial.println(stimulusDuration);
          Serial.print("Frequency: ");
          Serial.println(frequency);

          FlickerLED(frequency, stimulusDuration);
        }
        else if (FirstChar == "s") // sinusoidal dimming
        {
          stimulusDuration = atof(serialVals[1]);
          frequency = atof(serialVals[2]);
          Serial.println("Stim: Sinusoidal dimming");
          Serial.print("Stim duration: ");
          Serial.println(stimulusDuration);
          Serial.print("Frequency: ");
          Serial.println(frequency);

          SineLED(frequency, stimulusDuration);
        }

        else if (FirstChar == "cs") // contrast switching
        {
          stimulusDuration = atof(serialVals[1]);
          contrastSwitchTime = atof(serialVals[2]);
          ledUpdateTime = atof(serialVals[3]);
          Serial.println("Stim: Flicker");
          Serial.print("Stim duration: ");
          Serial.println(stimulusDuration);
          Serial.print("Contrast Switching Time: ");
          Serial.println(contrastSwitchTime);
          Serial.print("LED Update Time: ");
          Serial.println(ledUpdateTime);

          
          contrastSwitching(contrastSwitchTime, stimulusDuration, ledUpdateTime);
        }
        else if (FirstChar == "fsc") // flicker-sine convolution
        {
          stimulusDuration = atof(serialVals[1]);
          frequency = atof(serialVals[2]); // flicker frequency
          carrierFrequency = atof(serialVals[3]);
          Serial.println("Stim: Flicker-sine convolution");
          Serial.print("Stim duration: ");
          Serial.println(stimulusDuration);
          Serial.print("Flicker Frequency: ");
          Serial.println(frequency);
          Serial.print("Carrier Frequency: ");
          Serial.println(carrierFrequency);
          
          SineFreqConv(frequency, stimulusDuration, carrierFrequency);
        }
        else // not valid stimulus code
        {
          Serial.print(FirstChar);
          Serial.println(" is an invalid stimulus code");
        }
        //memset('\0', receivedChars, sizeof(receivedChars));
        memset(receivedChars, '\0', sizeof(receivedChars));
        //Serial.print("rc: ");
        //Serial.println(receivedChars);
        

}




// Stimuli
void FlickerLED(float FlickerFreq, float Duration)
{
  const long interval = 1000/(FlickerFreq*2);           // interval at which to blink (milliseconds)
  unsigned long previousMillis = 0;        // will store last time LED was updated
  unsigned long TimerStart = millis();        // will store last time LED was updated
  volatile byte ledState = LOW;

  bool runFunction = HIGH;
  while (runFunction)
  {
    unsigned long currentMillis = millis();
    if (currentMillis - previousMillis >= interval) {
    // save the last time you blinked the LED
    previousMillis = currentMillis;
    // if the LED is off turn it on and vice-versa:
    ledState = !ledState;
    digitalWrite(ledPin, ledState);
    }

    unsigned long TimerMillis = millis();
    if (TimerMillis-TimerStart >= Duration)
    {
      runFunction = LOW;
      digitalWrite(ledPin, LOW); // turn led off once done
      Serial.println("Stim done");
    }
  }
}

void SineLED(float SineFreq, float Duration)
{
  const long interval = 1000/(SineFreq);           // interval at which to blink (milliseconds)
  unsigned long previousMillis = 0;        // will store last time LED was updated
  unsigned long TimerStart = millis();        // will store last time LED was updated
  volatile byte ledState = LOW;

  bool runFunction = HIGH;
  while (runFunction)
  {
    int time = millis() % interval;              // returns a value between 0 and period;
    float angle = (PI * time) / interval;        // mapping to degrees
    int y = 100 * sin(angle);

    analogWrite(ledPin, y);

    unsigned long TimerMillis = millis();
    if (TimerMillis-TimerStart >= Duration)
    {
      runFunction = LOW;
      digitalWrite(ledPin, LOW); // turn led off once done
      Serial.println("Stim done");
    }
  }
}

void contrastSwitching(float contrastSwitchTime, float Duration, float updateTime)
{
  //const unsigned long contrastSwitchTime = 3000; // in ms
  //const unsigned long updateTime = 100; // in ms

  long randNumber;      // the variable which is supposed to hold the random number
  volatile byte contrast = LOW;

  unsigned long previousMillis = 0;        // will store last time LED was updated
  unsigned long switchPreviousMillis = 0;        // will store last time LED was updated

  unsigned long TimerStart = millis();        // will store last time LED was updated
  volatile byte ledState = LOW;

  bool runFunction = HIGH;
  while (runFunction)
  {
    unsigned long switchCurrentMillis = millis();
    if (switchCurrentMillis - switchPreviousMillis >= contrastSwitchTime) {
    switchPreviousMillis = switchCurrentMillis;

        // if the LED is off turn it on and vice-versa:
    contrast=!contrast;
    }
  
  // check if time to update LED and update
  unsigned long currentMillis = millis();
  if (currentMillis - previousMillis >= updateTime) {
    // save the last time you blinked the LED
    previousMillis = currentMillis;

  if (contrast==HIGH) 
  {
    randNumber = random(0, 255);
    analogWrite(ledPin, randNumber);         
  } else
    randNumber = random(64, 191);
    analogWrite(ledPin, randNumber);  
  }

  unsigned long TimerMillis = millis();
  if (TimerMillis-TimerStart >= Duration)
    {
      runFunction = LOW;
      digitalWrite(ledPin, LOW); // turn led off once done
      Serial.println("Stim done");
    }
}
}



void SineFreqConv(float flickerFreq, float Duration, float carrierFreq)
{
  const long interval = 1000 / (flickerFreq * 2);  // interval at which to blink (milliseconds)
  unsigned long TimerStart = millis();        // will store last time LED was updated
  unsigned long previousMillis = 0;  // will store last time LED was updated
  const long period = 1000/(carrierFreq);           // interval at which to blink (milliseconds)

  volatile byte ledState = LOW;


  bool runFunction = HIGH;
  while (runFunction)
  {
    // generate sine wave between 0 and 1
  int time = millis() % period;        // returns a value between 0 and period;
  float angle = (PI * time) / period;  // mapping to degrees
  float y = sin(angle);

  // get low and high luminance levels for sine wave-based contrast 
  float lowValue = 127 - y * 127;
  float highValue = 127 + y * 127;

  unsigned long currentMillis = millis();
  if (currentMillis - previousMillis >= interval) {
    // save the last time you blinked the LED
    previousMillis = currentMillis;
    ledState = !ledState;
    //Serial.println(ledState);

    if (ledState == 0) {
      analogWrite(ledPin, lowValue);
      //Serial.println(lowValue);

    } else {
      analogWrite(ledPin, highValue);
      //Serial.println(highValue);
    }
  }

    unsigned long TimerMillis = millis();
    if (TimerMillis-TimerStart >= Duration)
    {
      runFunction = LOW;
      digitalWrite(ledPin, LOW); // turn led off once done
      Serial.println("Stim done");
    }
  }
}

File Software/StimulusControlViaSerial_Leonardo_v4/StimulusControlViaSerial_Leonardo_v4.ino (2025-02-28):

#define CLOCK_FREQ 16000000  // Arduino Leonardo clock frequency (16 MHz)
#define TABLE_SIZE 256       // Number of samples in the wavetable


// gamma correction LUTs

// Declare a pointer to the current LUT
const uint16_t* currentLUT;
char GammaLUTName;

const uint16_t PROGMEM defaultLUT[1041] = {
 0, 1, 2, 3, 4, 5, 6, 7, 8, 9,
 10, 11, 12, 13, 14, 15, 16, 17, 18, 19,
 20, 21, 22, 23, 24, 25, 26, 27, 28, 29,
 30, 31, 32, 33, 34, 35, 36, 37, 38, 39,
 40, 41, 42, 43, 44, 45, 46, 47, 48, 49,
 50, 51, 52, 53, 54, 55, 56, 57, 58, 59,
 60, 61, 62, 63, 64, 65, 66, 67, 68, 69,
 70, 71, 72, 73, 74, 75, 76, 77, 78, 79,
 80, 81, 82, 83, 84, 85, 86, 87, 88, 89,
 90, 91, 92, 93, 94, 95, 96, 97, 98, 99,
 100, 101, 102, 103, 104, 105, 106, 107, 108, 109,
 110, 111, 112, 113, 114, 115, 116, 117, 118, 119,
 120, 121, 122, 123, 124, 125, 126, 127, 128, 129,
 130, 131, 132, 133, 134, 135, 136, 137, 138, 139,
 140, 141, 142, 143, 144, 145, 146, 147, 148, 149,
 150, 151, 152, 153, 154, 155, 156, 157, 158, 159,
 160, 161, 162, 163, 164, 165, 166, 167, 168, 169,
 170, 171, 172, 173, 174, 175, 176, 177, 178, 179,
 180, 181, 182, 183, 184, 185, 186, 187, 188, 189,
 190, 191, 192, 193, 194, 195, 196, 197, 198, 199,
 200, 201, 202, 203, 204, 205, 206, 207, 208, 209,
 210, 211, 212, 213, 214, 215, 216, 217, 218, 219,
 220, 221, 222, 223, 224, 225, 226, 227, 228, 229,
 230, 231, 232, 233, 234, 235, 236, 237, 238, 239,
 240, 241, 242, 243, 244, 245, 246, 247, 248, 249,
 250, 251, 252, 253, 254, 255, 256, 257, 258, 259,
 260, 261, 262, 263, 264, 265, 266, 267, 268, 269,
 270, 271, 272, 273, 274, 275, 276, 277, 278, 279,
 280, 281, 282, 283, 284, 285, 286, 287, 288, 289,
 290, 291, 292, 293, 294, 295, 296, 297, 298, 299,
 300, 301, 302, 303, 304, 305, 306, 307, 308, 309,
 310, 311, 312, 313, 314, 315, 316, 317, 318, 319,
 320, 321, 322, 323, 324, 325, 326, 327, 328, 329,
 330, 331, 332, 333, 334, 335, 336, 337, 338, 339,
 340, 341, 342, 343, 344, 345, 346, 347, 348, 349,
 350, 351, 352, 353, 354, 355, 356, 357, 358, 359,
 360, 361, 362, 363, 364, 365, 366, 367, 368, 369,
 370, 371, 372, 373, 374, 375, 376, 377, 378, 379,
 380, 381, 382, 383, 384, 385, 386, 387, 388, 389,
 390, 391, 392, 393, 394, 395, 396, 397, 398, 399,
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
};

const uint16_t PROGMEM GREENLUT[1041] = {
    0, 0, 0, 0, 0, 0, 0, 0, 0, 0, 
    0, 0, 0, 0, 0, 0, 0, 0, 0, 0, 
    0, 0, 0, 0, 0, 0, 1, 1, 1, 2, 
    2, 2, 3, 3, 3, 4, 4, 4, 5, 5, 
    5, 6, 6, 7, 7, 7, 8, 8, 8, 9, 
    9, 9, 10, 10, 10, 11, 11, 11, 12, 12, 
    12, 13, 13, 13, 14, 14, 14, 15, 15, 15, 
    15, 16, 16, 16, 17, 17, 17, 18, 18, 18, 
    19, 19, 19, 20, 20, 20, 21, 21, 21, 22, 
    22, 22, 23, 23, 23, 24, 24, 24, 25, 25, 
    25, 26, 26, 26, 27, 27, 27, 28, 28, 28, 
    29, 29, 29, 30, 30, 31, 31, 31, 32, 32, 
    32, 33, 33, 33, 34, 34, 34, 35, 35, 35, 
    36, 36, 36, 37, 37, 37, 38, 38, 38, 39, 
    39, 39, 40, 40, 40, 41, 41, 42, 42, 42, 
    42, 43, 43, 43, 44, 44, 44, 45, 45, 45, 
    46, 46, 46, 47, 47, 47, 47, 48, 48, 48, 
    49, 49, 49, 50, 50, 50, 51, 51, 51, 52, 
    52, 52, 53, 53, 53, 54, 54, 54, 55, 55, 
    55, 56, 56, 56, 57, 57, 57, 58, 58, 58, 
    59, 59, 59, 60, 60, 60, 61, 61, 61, 62, 
    62, 62, 63, 63, 63, 64, 64, 64, 65, 65, 
    65, 66, 66, 66, 67, 67, 67, 67, 68, 68, 
    68, 69, 69, 69, 70, 70, 70, 71, 71, 71, 
    72, 72, 72, 72, 73, 73, 73, 74, 74, 74, 
    75, 75, 75, 76, 76, 76, 77, 77, 77, 78, 
    78, 78, 79, 79, 79, 80, 80, 80, 81, 81, 
    81, 82, 82, 82, 83, 83, 83, 84, 84, 85, 
    85, 85, 86, 86, 86, 87, 87, 87, 88, 88, 
    88, 89, 89, 89, 90, 90, 90, 91, 91, 91, 
    92, 92, 92, 93, 93, 93, 94, 94, 94, 95, 
    95, 95, 96, 96, 96, 97, 97, 97, 97, 98, 
    98, 98, 99, 99, 99, 100, 100, 100, 101, 101, 
    101, 101, 102, 102, 102, 103, 103, 103, 104, 104, 
    104, 105, 105, 105, 106, 106, 106, 107, 107, 107, 
    108, 108, 108, 109, 109, 109, 110, 110, 110, 111, 
    111, 111, 112, 112, 112, 113, 113, 113, 114, 114, 
    114, 115, 115, 115, 116, 116, 116, 117, 117, 117, 
    117, 118, 118, 118, 119, 119, 119, 120, 120, 120, 
    121, 121, 121, 121, 122, 122, 122, 123, 123, 123, 
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

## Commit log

2023-11-20 create pcb for green leds
    [bom.csv, designators.csv, green_led_pcb.kicad_pcb, green_led_pcb.kicad_sch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]
2023-11-20 update greenled
    [green_led_pcb.kicad_pcb]
2023-11-20 update carvera files
    [green_led_pcb-B_Cu.gbr, green_led_pcb-B_Mask.gbr, green_led_pcb-B_Paste.gbr, green_led_pcb-B_SilkS.gbr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]
2023-11-20 update green pcb
    [green_led_pcb.kicad_sch]
2023-12-20 new board version
    [bom.csv, designators.csv, green_uv_led_pcb.kicad_pcb, green_uv_led_pcb.kicad_sch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]
2023-12-20 add gerbers folder
    [green_uv_led_pcb-B_Adhesive.gbr, green_uv_led_pcb-B_Courtyard.gbr, green_uv_led_pcb-B_Cu.gbr, green_uv_led_pcb-B_Fab.gbr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]
2024-04-08 preliminary 3d printing and simple arudino PWM stimulation code
    [101732.dxf, 101732.stp, 103105.dxf, 103105.stp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]
2024-04-09 basic serial -> flicker control
    [CustomRBracket_HolesAndMagnets.blend, CustomRBracket_HolesAndMagnets.stl, CustomRBracket_HolesAndMagnets_PREHOLES.blend, CustomRBracket_HolesAndMagnets_PREHOLE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]
2024-04-11 clean up 3d printing
    [CustomRBracket_HolesAndMagnets.blend, CustomRBracket_HolesAndMagnets.stl, CustomRBracket_HolesAndMagnets_PREHOLES.blend, CustomRBracket_HolesAndMagnets_PREHOLE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]
2024-04-18 move pcbs to dedicated folder and start creating led driver pcb
    [bom.csv, designators.csv, green_led_pcb-B_Cu.gbr, green_led_pcb-B_Mask.gbr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]
2024-06-07 update led der
    [bom.csv, designators.csv, green_led_pcb-B_Cu.gbr, green_led_pcb-B_Mask.gbr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]
2024-10-25 added full panel pcb
    [Full panel.kicad_pcb, Full panel.kicad_sch]
2024-10-25 updated the full panell schematic
    [Full panel.kicad_pcb, LEDs+driver.kicad_pcb, LEDs+driver.kicad_sch]
2024-10-30 Full Pannel With lt3519 for low voltage application
    [Full panel.kicad_pcb]
2024-11-27 All work update
    [101732.dxf, 101732.stp, 103105.dxf, 103105.stp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]
2025-01-20 added custom led driver PCB
    [custom_driver-B_Cu.gbr, custom_driver-B_Mask.gbr, custom_driver-B_Paste.gbr, custom_driver-B_Silkscreen.gbr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]
2025-01-22 upgraded the circuit and the gerber files
    [custom_driver-B_Cu.gbr, custom_driver-B_Mask.gbr, custom_driver-B_Paste.gbp, custom_driver-B_Paste.gbr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]
2025-02-27 update arduino stimulus generation code

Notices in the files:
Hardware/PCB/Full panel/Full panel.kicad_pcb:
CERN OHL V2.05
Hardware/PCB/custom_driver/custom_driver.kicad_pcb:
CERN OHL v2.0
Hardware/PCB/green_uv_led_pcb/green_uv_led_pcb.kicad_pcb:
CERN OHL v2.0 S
